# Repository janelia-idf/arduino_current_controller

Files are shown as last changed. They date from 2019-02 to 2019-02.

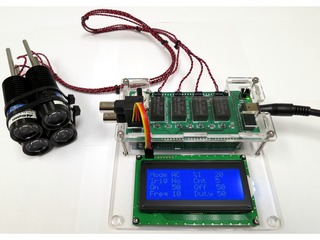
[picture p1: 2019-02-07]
images/arduino_current_controller_03_s.jpg

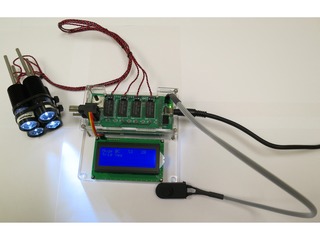
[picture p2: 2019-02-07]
images/arduino_current_controller_01_s.jpg

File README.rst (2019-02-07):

==========================
Arduino Current Controller
==========================

Arduino-based current controller for drives with step/direction interface.

host
====

Contains the code for controlling with a host computer.

python
------

See host/python/README.rst

matlab
------

See host/matlab/README.rst

firmware
========

Contains the Arduino firmware files. See firmware/README.rst

pcb
===

Contains the arduino_current_controller pcb Kicad and gerber files.

Author: Peter Polidoro

This program is free software: you can redistribute it and/or modify
it under the terms of the GNU Lesser General Public License as published by
the Free Software Foundation, either version 3 of the License, or
(at your option) any later version.

This program is distributed in the hope that it will be useful,
but WITHOUT ANY WARRANTY; without even the implied warranty of
MERCHANTABILITY or FITNESS FOR A PARTICULAR PURPOSE.  See the
GNU Lesser General Public License for more details.

You should have received a copy of the GNU Lesser General Public License
along with this program.  If not, see <http://www.gnu.org/licenses/>.

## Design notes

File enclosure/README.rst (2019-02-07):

====================================
arduino_current_controller enclosure
====================================

* Press eight #4 pem nuts and four #6 pem nuts into 0.25" thick base
  plate.

* Press two #6 pem nuts into 0.125" side plate.

* Attach (pcb + arduino) to 0.25" thick base plate.

* Connect a 1k resistor between IM483 P2:1 and P2:2. Connect a 1.6k
  resistor between P2:2 and P2:3.

* Attach IM483 to 0.25" thick base plate 6-32 x 1/2" socket head cap
  screws.

* Cut 4-pin 12" jumper wires 3" from connector. Separate wires back 1"
  and strip wires 1/4".

* Connect RED to IM483 P1:5, ORANGE to P1:4, YELLOW to P1:3, and
  GREEN to P1:2.

* Plug 4-pin connector to P2 on pcb.

* Set IM483 current resolution switch to OFF, OFF, OFF, ON, to set
  resolution to 256 microsteps/step.

* Cut UNSHIELDED 22AWG 2 COND to 3" and remove outer gray
  insulation. Solder to CONN JACK 2.5x5.5MM, RED to center, BLACK to
  terminal next to center terminal, and cut off the 3rd terminal. Cut
  wire insulation 1/8" on CONN JACK side and 1/4" on other side. Use
  3/32" x 1/2" heat shrink tubing.

* Screw CONN JACK 2.5x5.5MM into 0.125" side plate hole.

* Cut UNSHIELDED 22AWG 4 COND to 2" and remove outer gray
  insulation. BLACK: 2", GREEN: 1 7/8", WHITE: 1 3/4", RED: 1
  5/8". Cut wire insulation 1/4" on both sides. Solder to TERMINAL PB
  4CIRC 2.50" MOUNT, BLACK closest to PCB, then GREEN, then WHITE,
  then RED. With a BLUE marker, color WHITE until BLUE. Use 1/8" x
  3/4" heat shrink tubing.

* Screw TERMINAL PB 4CIRC into 0.125" side plate with two 6-32 x 3/8"
  socket head cap screws with a #6 washer on each.

* Connect TERMINAL PB 4CIRC BLACK to P2:5, GREEN to P2:6, BLUE to
  P2:7, and RED to P2:8.

* Connect CONN JACK BLACK to PCB P3:GND and CONN JACK RED to PCB
  P3:+24VDC.

* Cut another UNSHIELDED 22AWG 2 COND to 3" and remove
  insulation. Connect BLACK to PCB P3:GND and RED to PCB P3:+24VDC.

* Connect BLACK to IM483 P2:3 and RED to IM483 P2:4.

* Place colored tape on spring terminal tops, BLACK, GREEN, and
  BLUE. (the RED terminal is already RED).

Author: Peter Polidoro

This program is free software: you can redistribute it and/or modify
it under the terms of the GNU Lesser General Public License as published by
the Free Software Foundation, either version 3 of the License, or
(at your option) any later version.

This program is distributed in the hope that it will be useful,
but WITHOUT ANY WARRANTY; without even the implied warranty of
MERCHANTABILITY or FITNESS FOR A PARTICULAR PURPOSE.  See the
GNU Lesser General Public License for more details.

You should have received a copy of the GNU Lesser General Public License
along with this program.  If not, see <http://www.gnu.org/licenses/>.

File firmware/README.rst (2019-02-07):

Arduino Current Controller Device Firmware
------------------------------------------

Arduino firmware for the arduino_current_controller device.

For see the INSTALL.rst for installation instructions.

arduino_current_controller device firmware may be freely distributed and
modified in accordance with the License.

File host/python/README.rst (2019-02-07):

==========================
arduino_current_controller
==========================

arduino_current_controller is a python package to control the Arduino
current controller over USB, using the python module, the command
line, or a webpage using a webserver.

Install
=======

See INSTALL.rst

Running
=======

* If installed into a virtual environment, activate the virtual
  environment before running::

    source ~/virtualenvs/arduino_current_controller/bin/activate

Python Module
-------------

Typical usage often looks like this::

    from arduino_current_controller import ArduinoCurrentController

    acc = ArduinoCurrentController()
    acc.getArduinoCurrentControllerInfo()
    acc.turnOnAll(40)
    acc.turnOffAll()
    acc.StartPwmAll(40,1000,1000)
    acc.StopPwmAll()

Web Page Controls
-----------------

Open a terminal and run::

    arduino_current_controller_webserver.py

Open a browser and navigate to::

    http://localhost:5000

Author: Peter Polidoro

This program is free software: you can redistribute it and/or modify
it under the terms of the GNU Lesser General Public License as published by
the Free Software Foundation, either version 3 of the License, or
(at your option) any later version.

This program is distributed in the hope that it will be useful,
but WITHOUT ANY WARRANTY; without even the implied warranty of
MERCHANTABILITY or FITNESS FOR A PARTICULAR PURPOSE.  See the
GNU Lesser General Public License for more details.

You should have received a copy of the GNU Lesser General Public License
along with this program.  If not, see <http://www.gnu.org/licenses/>.

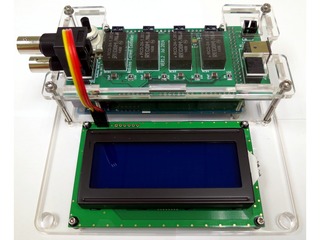
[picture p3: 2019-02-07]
images/arduino_current_controller_04_s.jpg

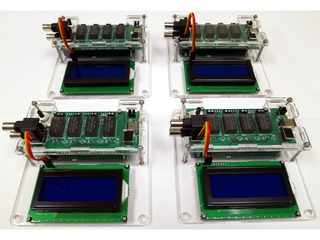
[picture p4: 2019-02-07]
images/arduino_current_controller_08_s.jpg

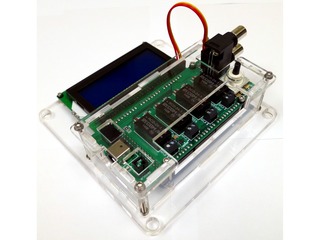
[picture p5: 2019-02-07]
images/arduino_current_controller_05_s.jpg

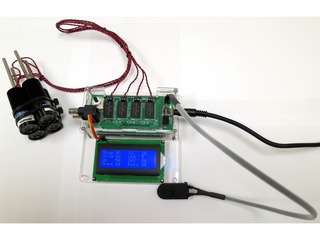
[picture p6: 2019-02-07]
images/arduino_current_controller_02_s.jpg

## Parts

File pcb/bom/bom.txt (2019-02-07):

-*- mode:org -*-

# Opt101.lst
| ref     | value                    |
|---------+--------------------------|
| C1      | 10uF                     |
| C2      | 10uF                     |
| C3      | 10uF                     |
| C4      | 10uF                     |
| C5      | 10uF                     |
| C6      | 10uF                     |
| C7      | 10uF                     |
| C8      | 0.1uF                    |
| D1      | LED                      |
| E1      | ENCODER_62P              |
| K1      | DISPLAY                  |
| P1      | OUT_A                    |
| P2      | OUT_B                    |
| P3      | OUT_C                    |
| P4      | OUT_D                    |
| P5      | +24VDC                   |
| P6      | BNC_IN                   |
| P7      | SWITCH_IN                |
| R1      | 150                      |
| R2      | 150                      |
| R3      | 150                      |
| R4      | 150                      |
| R5      | 1.96k                    |
| R6      | 150                      |
| RCD1    | RCD-24                   |
| RCD2    | RCD-24                   |
| RCD3    | RCD-24                   |
| RCD4    | RCD-24                   |
| REG1    | CONV_DC_DC               |
| SHIELD1 | ARDUINO_MEGA_SHIELD_FULL |
| U1      | SSR_DC_6PIN              |
| U2      | SSR_DC_6PIN              |
| U3      | SSR_DC_6PIN              |
| U4      | SSR_DC_6PIN              |
| U5      | MAX6817                  |

# Bill of Materials
| ! | part    | description                                                     | vendor      | part number               | quantity |   cost |
|---+---------+-----------------------------------------------------------------+-------------+---------------------------+----------+--------|
|   | PCB     | arduino_current_controller                                      | pcbuniverse | v1.2                      |        1 |   1.00 |
|   | C1-7    | CAP CER 10UF 50V 10% X7S 1210                                   | digikey     | 445-4536-1-ND             |        7 |   1.24 |
|   | C8      | CAP CER 0.1UF 50V 10% X7R 1210                                  | digikey     | 478-3586-1-ND             |        1 |   0.39 |
|   | D1      | LED GREEN CLEAR 0805 SMD                                        | digikey     | 160-1179-1-ND             |        1 |   0.35 |
|   | E1      | ENCODER OPT LO TORQ PB 16POS PC                                 | digikey     | GH7296-ND                 |        1 |   7.47 |
|   | E1      | KNOB CLR/MATTE .50"DIA 6MM SHAFT                                | digikey     | 226-3092-ND               |        1 |   5.36 |
|   | K1      | LCD SERIAL 4X20 SIDE WHT BKLT                                   | digikey     | NHD-0420D3Z-NSW-BBW-V3-ND |        1 |  25.90 |
|   | K1      | Jumper Wire - 0.1", 3-pin, 4"                                   | sparkfun    | PRT-10363                 |        1 |   0.95 |
|   | K1      | CONN HEADER 50POS .100" SGL GOLD                                | digikey     | SAM1031-50-ND             |        1 |   3.33 |
|   | P1-4    | TERMINAL BLOCK 3.5MM 2POS PCB                                   | digikey     | ED1514-ND                 |        4 |   0.63 |
|   | P5      | CONN PWR JACK DC 2.5X5.5 8A T/H                                 | digikey     | CP-063BH-ND               |        1 |   1.78 |
|   | P5      | POWER SUPPLY SWITCHER 101W 24V                                  | digikey     | 271-2731-ND               |        1 |  81.38 |
|   | P6      | CONN BNC JACK R/A 75 OHM PCB                                    | digikey     | ACX1655-ND                |        1 |  11.10 |
|   | P7      | CONN HEADER 2POS .100 VERT GOLD                                 | digikey     | WM4800-ND                 |        1 |   0.88 |
|   | P7      | UNSHIELDED 22AWG 2 COND                                         | digikey     | W120-100-ND               |        1 |   0.20 |
|   | P7      | CONN HOUSING 2POS .100 W/LATCH                                  | digikey     | WM2900-ND                 |        1 |   0.49 |
|   | P7      | CONN HOUSING MALE 2POS .100                                     | digikey     | WM2533-ND                 |        1 |   0.79 |
|   | P7      | CONN TERM FEMALE 22-24AWG GOLD                                  | digikey     | WM2570-ND                 |        2 |   0.34 |
|   | P7      | CONN TERM MALE 22-24AWG GOLD                                    | digikey     | WM2567-ND                 |        2 |   0.37 |
|   | P7      | Pendant Switch with Cable, Push-Button, 1 NO, 5 Amps at 120V AC | mcmaster    | 6944K11                   |        1 |  18.89 |
|   | R1-4,6  | RES 150 OHM 1/2W 1% 1210 SMD                                    | digikey     | P150AACT-ND               |        5 |   0.51 |
|   | R5      | RES 1.96K OHM 1/2W 1% 1210 SMD                                  | digikey     | 541-1.96KAACT-ND          |        1 |   2.89 |
|   | RCD1-4  | LED SUPP CC BUCK 3-31V 1.2A 6DIP                                | digikey     | 945-1132-ND               |        4 |  15.32 |
|   | RCD1-4  | CONN SOCKET RCPT .014-.026 30AU                                 | digikey     | A32374-ND                 |       24 |   0.77 |
|   | REG1    | CONV DC/DC 1A 12V OUT SIP VERT                                  | digikey     | 945-1392-5-ND             |        1 |   8.79 |
|   | SHIELD1 | BOARD MCU MEGA2560                                              | digikey     | 1050-1018-ND              |        1 |  51.91 |
|   | SHIELD1 | CONN HDR VERT 50POS .100" SNGL                                  | digikey     | SAM1055-50-ND             |        4 |   3.42 |
|   | U1-4    | RELAY SSR SPST SGL 2.5A 6SMD GW                                 | digikey     | 516-2367-5-ND             |        4 |   6.05 |
|   | U5      | IC DEBOUNCER SWITCH DUAL SOT23-6                                | digikey     | MAX6817EUT+TCT-ND         |        1 |   5.25 |
|---+---------+-----------------------------------------------------------------+-------------+---------------------------+----------+--------|
| # | total   |                                                                 |             |                           |          | 353.12 |
#+TBLFM: @31$7=(@I$quantity..@II$quantity)*(@I$cost..@II$cost);%.2f;N

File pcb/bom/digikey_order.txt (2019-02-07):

40, 445-4536-1-ND
20, 478-3586-1-ND
20, 160-1179-1-ND
10, GH7296-ND
10, 226-3092-ND
10, NHD-0420D3Z-NSW-BBW-V3-ND
20, SAM1031-50-ND
50, ED1514-ND
10, CP-063BH-ND
5, 271-2731-ND
60, P150AACT-ND
20, 541-1.96KAACT-ND
12, 945-1132-ND
200, A32374-ND
4, 1050-1018-ND
30, SAM1055-50-ND
20, 516-2367-5-ND
20, MAX6817EUT+TCT-ND
10, 945-1392-5-ND

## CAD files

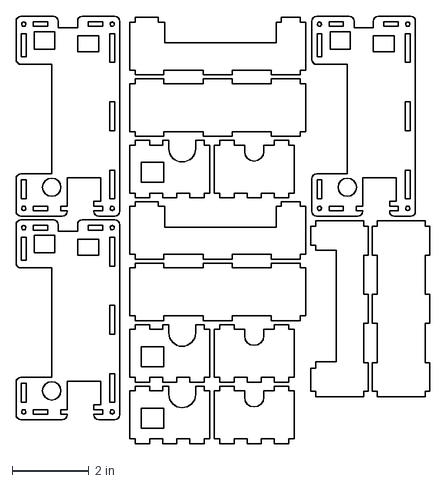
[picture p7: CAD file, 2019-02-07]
enclosure/arduino_enclosure_current_controller.125in.array.dxf
10.8 x 11.1 in

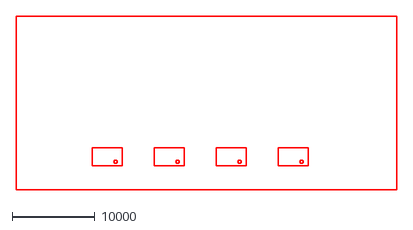
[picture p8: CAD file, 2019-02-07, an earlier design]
pcb/v1.0/dxf/arduino_current_controller-SilkS_Back.dxf
46000.0 x 21000.0

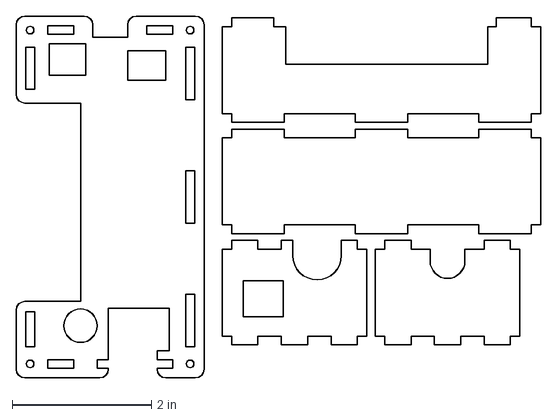
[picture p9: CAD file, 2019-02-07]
enclosure/arduino_enclosure_current_controller.125in.dxf
7.54 x 5.20 in

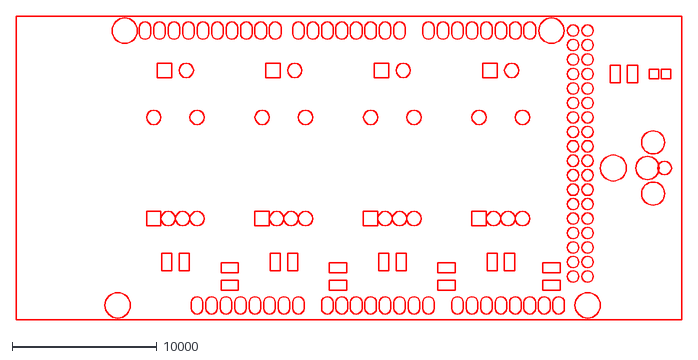
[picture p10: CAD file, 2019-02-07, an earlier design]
pcb/v1.0/dxf/arduino_current_controller-Mask_Front.dxf
46000.0 x 21000.0

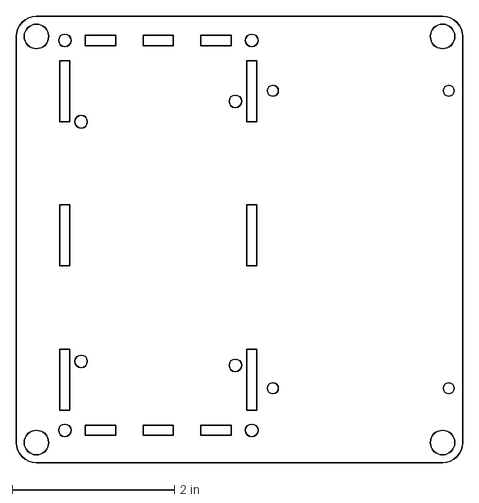
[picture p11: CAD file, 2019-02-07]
enclosure/arduino_relay_mfc_controller_enclosure_display.25in.dxf
5.50 x 5.50 in

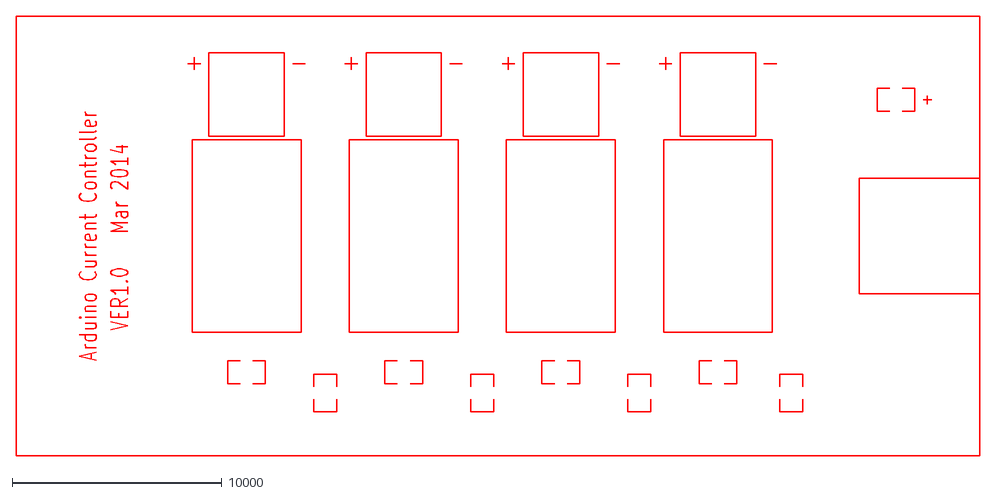
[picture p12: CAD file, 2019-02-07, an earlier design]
pcb/v1.0/dxf/arduino_current_controller-SilkS_Front.dxf
46000.0 x 21000.0

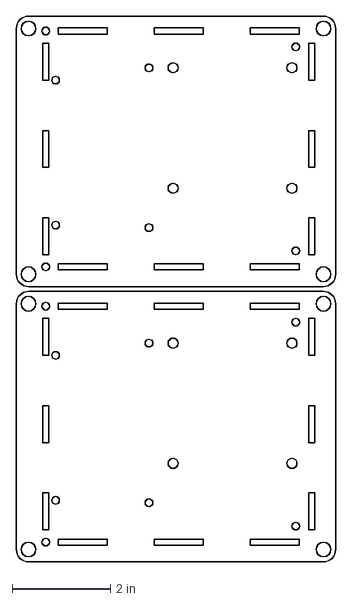
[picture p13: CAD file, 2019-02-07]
enclosure/arduino_enclosure_current_controller.25in.array.dxf
6.50 x 11.1 in

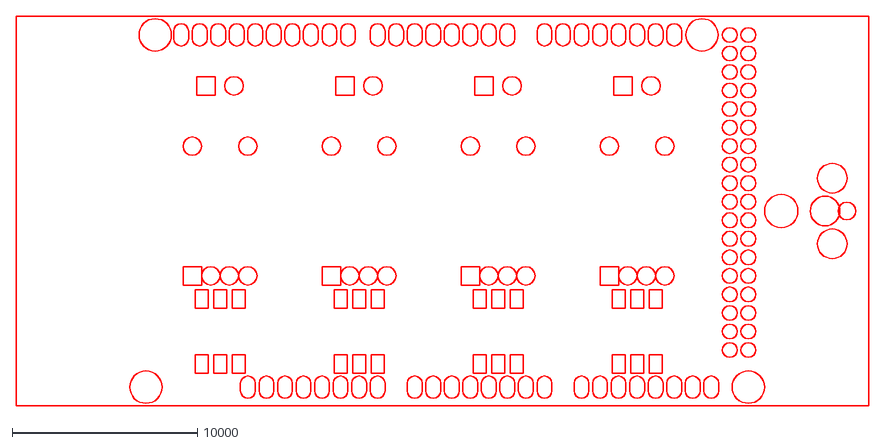
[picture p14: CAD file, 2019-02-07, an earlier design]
pcb/v1.0/dxf/arduino_current_controller-Mask_Back.dxf
46000.0 x 21000.0

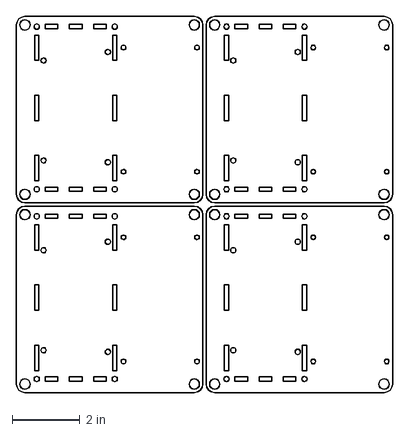
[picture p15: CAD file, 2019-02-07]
enclosure/arduino_relay_mfc_controller_enclosure_display.25in.array.dxf
11.1 x 11.1 in

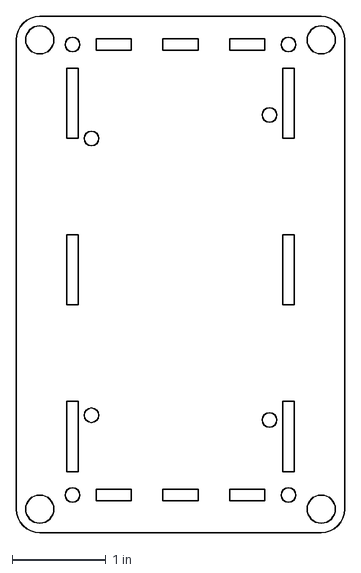
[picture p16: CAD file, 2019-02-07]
enclosure/arduino_enclosure_current_controller.25in.dxf
3.50 x 5.50 in

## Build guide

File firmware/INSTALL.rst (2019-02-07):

Firmware installation instructions
-----------------------------------

Requirements:

The following libraries should be placed in the arduino sketchbook libraries
directory.

* Streaming         https://bitbucket.org/peterpolidoro/arduino_libs/src
* SerialReceiver    https://bitbucket.org/peterpolidoro/arduino_libs/src
* DictPrinter       https://bitbucket.org/peterpolidoro/arduino_libs/src
* TimerOne          https://bitbucket.org/peterpolidoro/arduino_libs/src

Build and upload the firmware using the Arduino IDE.

see http://arduino.cc/en/Guide/Environment for instructions on using the IDE.

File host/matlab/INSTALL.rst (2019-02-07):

Matlab Arduino Current Controller Installation Instructions
-----------------------------------------------------------

* First make sure Arduino software is installed and Arduino board is
  connected with a USB cable

* If not, follow the README.rst instructions on this page:
  https://bitbucket.org/peterpolidoro/arduino_current_controller

* Then add the
  arduino_current_controller/host/matlab/arduino_current_controller
  directory and all subdirectorys to the Matlab path.

* Examples can be found in the
  arduino_current_controller/host/matlab/examples directory.

* For documentation on the ArduinoCurrentController object type: "help
  ArduinoCurrentController" at the Matlab command prompt.

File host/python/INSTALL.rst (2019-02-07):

arduino_current_controller installation instructions
----------------------------------------------------

* Create a new virtual environment if necessary::

    virtualenv --system-site-packages ~/virtualenvs/arduino_current_controller

* Activate a virtual environment::

    source ~/virtualenvs/arduino_current_controller/bin/activate

* Install dependencies for webpage controller::

    pip install flask --upgrade
    pip install flask-sijax --upgrade

* Clone bitbucket mercurial repositories::

    mkdir ~/mercurial
    cd ~/mercurial
    hg clone https://bitbucket.org/peterpolidoro/python_libs/
    hg clone https://bitbucket.org/peterpolidoro/arduino_current_controller/

* Install python packages::

    cd ~/mercurial/python_libs/arduino_device
    python cleanup.py
    python setup.py install
    cd ~/mercurial/arduino_current_controller/host/python
    python cleanup.py
    python setup.py install

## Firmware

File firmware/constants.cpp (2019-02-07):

#include "constants.h"
namespace constants {
  // Communications parameters
  const int baudrate = 9600;

  // Device parameters
  const int modelNumber = 2346;
  const int serialNumberMin = 0;
  const int serialNumberMax = 255;
  const int firmwareNumber = 0;

  // Pin assignment
  const int enablePinArray[CHANNEL_COUNT] = {5,6,11,12};
  const int pwmPinArray[CHANNEL_COUNT] = {7,8,9,10};
  const int switchInterruptPin = 18;
  const int bncAPin = 21;
  const int bncBPin = 20;
  const int encoderAPin = 2;
  const int encoderBPin = 3;
  const int encoderBtnInterruptPin = 19;

  // Current parameters
  const int percentCurrentMin = 0;
  const int percentCurrentMax = 100;
  const int percentCurrentDefault = 20;
  const int percentCurrentInc = 1;
  const int analogOutMin = 255;
  const int analogOutMax = 0;

  // Pwm parameters
  const int durationMin = 1;
  const int durationMax = 100;
  const int durationDefault = 50;
  const int durationInc = 1;
  const int countMin = 1;
  const int countMax = 50;
  const int countDefault = 5;
  const int countInc = 1;
  const int frequencyMin = 1000/(2*durationMax);
  const int frequencyMax = 1000/(2*durationMin);
  const int dutyCycleMin = 1;
  const int dutyCycleMax = 99;

  // Display parameters
  const int displayPeriod = 300;
  const int displayFieldLength = 4;

  // External Interrupts
  const int switchInterruptNumber = 5;
  const int bncInterruptNumber = 2;
  const int encoderBtnInterruptNumber = 4;

}

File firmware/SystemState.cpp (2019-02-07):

#if defined(ARDUINO) && ARDUINO >= 100
#include "Arduino.h"
#else
#include "WProgram.h"
#endif
#include "string.h"
#include "SystemState.h"

SystemState::SystemState() {
  setErrMsg("");
}

void SystemState::setErrMsg(char *msg) {
  strncpy(errMsg,msg,SYS_ERR_BUF_SZ);
}

void SystemState::initialize() {
  tts.init();
  for (int channel=0;channel<constants::CHANNEL_COUNT;channel++) {
    pinMode(constants::enablePinArray[channel], OUTPUT);
    pwmTasks[channel].onTaskId = -1;
    pwmTasks[channel].offTaskId = -1;
    turnOff(channel);
  }

  turned_on = false;
  mode_prev = encoderVariables.getMode();

  // Display
  display = NewhavenDisplay();
  initializeDisplay();

  // Interrupts
  pinMode(constants::switchInterruptPin,INPUT);
  digitalWrite(constants::switchInterruptPin,HIGH);
  attachInterrupt(constants::switchInterruptNumber,switchISR,FALLING);

  pinMode(constants::bncAPin,INPUT);
  digitalWrite(constants::bncAPin,HIGH);
  attachInterrupt(constants::bncInterruptNumber,bncISR,FALLING);

  pinMode(constants::encoderBtnInterruptPin,INPUT);
  digitalWrite(constants::encoderBtnInterruptPin,HIGH);
  attachInterrupt(constants::encoderBtnInterruptNumber,encoderBtnISR,FALLING);

  // Outputs
  pinMode(constants::bncBPin,OUTPUT);
  digitalWrite(constants::bncBPin,LOW);

}

void SystemState::enable() {
  for (int channel=0;channel<constants::CHANNEL_COUNT;channel++) {
    enable(channel);
  }
}

void SystemState::enable(int channel) {
  enabled[channel] = true;
  digitalWrite(constants::enablePinArray[channel],HIGH);
}

void SystemState::disable() {
  for (int channel=0;channel<constants::CHANNEL_COUNT;channel++) {
    disable(channel);
  }
}

void SystemState::disable(int channel) {
  enabled[channel] = false;
  digitalWrite(constants::enablePinArray[channel],LOW);
}

void SystemState::setPercentCurrent(int percent_current) {
  for (int channel=0;channel<constants::CHANNEL_COUNT;channel++) {
    setPercentCurrent(percent_current,channel);
  }
}

void SystemState::setPercentCurrent(int percent_current, int channel) {
  int analog_out = map(percent_current,
                       constants::percentCurrentMin,
                       constants::percentCurrentMax,
                       constants::analogOutMin,
                       constants::analogOutMax);
  analogWrite(constants::pwmPinArray[channel],analog_out);
}

void SystemState::turnOn() {
  for (int channel=0;channel<constants::CHANNEL_COUNT;channel++) {
    turnOn(encoderVariables.getPercentCurrent(channel));
  }
}

void SystemState::turnOn(int percent_current) {
  for (int channel=0;channel<constants::CHANNEL_COUNT;channel++) {
    turnOn(percent_current, channel);
  }
}

void SystemState::turnOn(int percent_current, int channel) {
  turnOff(channel);
  setPercentCurrent(percent_current, channel);
  enable(channel);
  turned_on = true;
  digitalWrite(constants::bncBPin,HIGH);
}

void SystemState::turnOff() {
  for (int channel=0;channel<constants::CHANNEL_COUNT;channel++) {
    turnOff(channel);
  }
}

void SystemState::turnOff(int channel) {
  stopPwm(channel);
}

void SystemState::startPwm() {
  for (int channel=0;channel<constants::CHANNEL_COUNT;channel++) {
    startPwm(encoderVariables.getPercentCurrent(channel),
             encoderVariables.getDurationOn(channel),
             encoderVariables.getDurationOff(channel),
             encoderVariables.getCount(channel),
             channel);
  }
}

void SystemState::startPwm(int percent_current, int duration_on, int duration_off, int count) {
  for (int channel=0;channel<constants::CHANNEL_COUNT;channel++) {
    startPwm(percent_current, duration_on, duration_off, count, channel);
  }
}

void SystemState::startPwm(int percent_current, int duration_on, int duration_off, int count, int channel) {
  turnOff(channel);
  setPercentCurrent(percent_current, channel);
  long period = duration_on + duration_off;
  if (channel == 0) {
    pulseCount = 0;
    pulseLimit = count;
  }
  pwmTasks[channel].onTaskId = (int)tts.addTaskUsingDelay(100,inlineSetPwmOn,channel,period,(long)count,false);
  pwmTasks[channel].offTaskId = (int)tts.addTaskUsingOffset((uint8_t)pwmTasks[channel].onTaskId,(uint32_t)duration_on,inlineSetPwmOff,channel,period,(long)count,false);
}

void SystemState::stopPwm() {
  for (int channel=0;channel<constants::CHANNEL_COUNT;channel++) {
    stopPwm(channel);
  }
}

void SystemState::stopPwm(int channel) {
  int onTaskId = pwmTasks[channel].onTaskId;
  int offTaskId = pwmTasks[channel].offTaskId;
  if (0 <= onTaskId) {
    tts.removeTask((uint8_t)onTaskId);
    pwmTasks[channel].onTaskId = -1;
  }
  if (0 <= offTaskId) {
    tts.removeTask((uint8_t)offTaskId);
    pwmTasks[channel].offTaskId = -1;
  }
  // setPercentCurrent(constants::percentCurrentMin, channel);
  disable(channel);
  turned_on = false;
  if (channel == 0) {
    digitalWrite(constants::bncBPin,LOW);
    pulseCount = 0;
    pulseLimit = 0;
  }
}

void SystemState::initializeDisplay() {
  display.init();
  delay(100);
  labelDisplay();
  displayEnabled = true;
  display.blinkingCursorOn();
}

void SystemState::labelDisplay() {
  display.clearScreen();
  display.setCursor(0,0);
  display.printPadRight("Mode",constants::displayFieldLength);
  display.setCursor(0,10);
  display.printPadRight("%I",constants::displayFieldLength);
  display.setCursor(1,0);
  display.printPadRight("Trig",constants::displayFieldLength);
  switch (encoderVariables.getMode()) {
  case constants::AC: {
    display.setCursor(1,10);
    display.printPadRight("Cnt",constants::displayFieldLength);
    display.setCursor(2,0);
    display.printPadRight("On",constants::displayFieldLength);
    display.setCursor(2,10);
    display.printPadRight("Off",constants::displayFieldLength);
    display.setCursor(3,0);
    display.printPadRight("Freq",constants::displayFieldLength);
    display.setCursor(3,10);
    display.printPadRight("Duty",constants::displayFieldLength);
  } break;
  }
  time_last_display_update = millis();
}

void SystemState::updateDisplay() {
  if (displayEnabled) {
    unsigned long time_now = millis();
    if ((time_now - time_last_display_update) > constants::displayPeriod) {
      time_last_display_update = time_now;
      mode = encoderVariables.getMode();

      display.setCursor(0,15);
      display.printPadRight(String(encoderVariables.getPercentCurrent()),constants::displayFieldLength);
      switch (mode) {
      case constants::AC: {
        int duration_on = encoderVariables.getDurationOn();
        int duration_off = encoderVariables.getDurationOff();
        display.setCursor(0,5);
        display.printPadRight("AC",constants::displayFieldLength);
        display.setCursor(1,5);
        if (tts.activeTasks()) {
          display.printPadRight("Yes",constants::displayFieldLength);
        } else {
          display.printPadRight("No",constants::displayFieldLength);
        }
        display.setCursor(1,15);
        display.printPadRight(String(encoderVariables.getCount()),constants::displayFieldLength);
        display.setCursor(2,5);
        display.printPadRight(String(duration_on),constants::displayFieldLength);
        display.setCursor(2,15);
        display.printPadRight(String(duration_off),constants::displayFieldLength);
        display.setCursor(3,5);
        int period = duration_on + duration_off;
        if (period > 1000) {
          display.printPadRight("<1",constants::displayFieldLength);
        } else {
          int freq = (int)(encoderVariables.getFrequency() + 0.5);
          display.printPadRight(String(freq),constants::displayFieldLength);
        }
        display.setCursor(3,15);
        int duty_cycle = (int)(encoderVariables.getDutyCycle() + 0.5);
        display.printPadRight(String(duty_cycle),constants::displayFieldLength);
      } break;
      case constants::DC: {
        display.setCursor(0,5);
        display.printPadRight("DC",constants::displayFieldLength);
        display.setCursor(1,5);
        if (turned_on) {
          display.printPadRight("Yes",constants::displayFieldLength);
        } else {
          display.printPadRight("No",constants::displayFieldLength);
        }
      } break;
      }
    }
    switch (encoderVariables.getVariableActive()) {
    case EncoderVariables::MODE:
      display.setCursor(0,5);
      break;
    case EncoderVariables::PERCENT_CURRENT:
      display.setCursor(0,15);
      break;
    case EncoderVariables::DURATION_ON:
      display.setCursor(2,5);
      break;
    case EncoderVariables::DURATION_OFF:
      display.setCursor(2,15);
      break;
    case EncoderVariables::COUNT:
      display.setCursor(1,15);
      break;
    case EncoderVariables::FREQUENCY:
      display.setCursor(3,5);
      break;
    case EncoderVariables::DUTY_CYCLE:
      display.setCursor(3,15);
      break;
    }
  }
}

void SystemState::update() {
  encoderVariables.update();
  mode = encoderVariables.getMode();
  if (mode != mode_prev) {
    mode_prev = mode;
    turnOff();
    labelDisplay();
  }
  updateDisplay();
  if (encoderVariables.getMode() == constants::DC) {
    if (turned_on) {
      setPercentCurrent(encoderVariables.getPercentCurrent());
    }
  }
}

void SystemState::handleSetPwmOn(int channel) {
  if (channel == 0) {
    if (pulseCount == 0) {
      digitalWrite(constants::bncBPin,HIGH);
    }
    pulseCount++;
  }
  enable(channel);
}

void SystemState::handleSetPwmOff(int channel) {
  if ((channel == 0) && (pulseCount == pulseLimit)) {
    digitalWrite(constants::bncBPin,LOW);
    pulseCount = 0;
    pulseLimit = 0;
  }
  disable(channel);
}

void SystemState::handleTriggerInterrupt() {
  switch (encoderVariables.getMode()) {
  case constants::AC: {
    if (!tts.activeTasks()) {
      startPwm();
    } else {
      stopPwm();
    }
  } break;
  case constants::DC: {
    if (!turned_on) {
      turnOn();
    } else {
      turnOff();
    }
  } break;
  }
}

void SystemState::handleEncoderBtnInterrupt() {
  encoderVariables.incVariableActive();
}


SystemState systemState;
